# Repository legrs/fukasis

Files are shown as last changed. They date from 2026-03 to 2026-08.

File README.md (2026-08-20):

<h3 align="center" style="margin:0;"> FUKASIS</h3>
<p align="center"> <strong>F</strong>ree <strong>U</strong>niversal <strong>K</strong>it for <strong>A</strong>stro-<strong>S</strong>pectroscopic <strong>I</strong>maging <strong>S</strong>ystem </p>

<p align="right">最終更新日：2026 08/20</p>

<!--### このrepositoryは現在整備途中です。完了するまでしばらくお待ちください。 2026/3/31-->

このREADME.mdはかなり長くなってしまいました。右上にあるGithubの目次機能などを使うと読みやすくなると思います

## はじめに Introduction

**天体用低分散分光システム FUKASIS** は、安価かつ手軽に運用可能な、オープンソースの天体観測用の簡易分光システムです。

<table style="border:1px solid #00000000; font-weight:900; font-size:0.8rem;">
  <tr style="border:1px solid #00000000;">
    <td align="center" style="border:1px solid #00000000;">
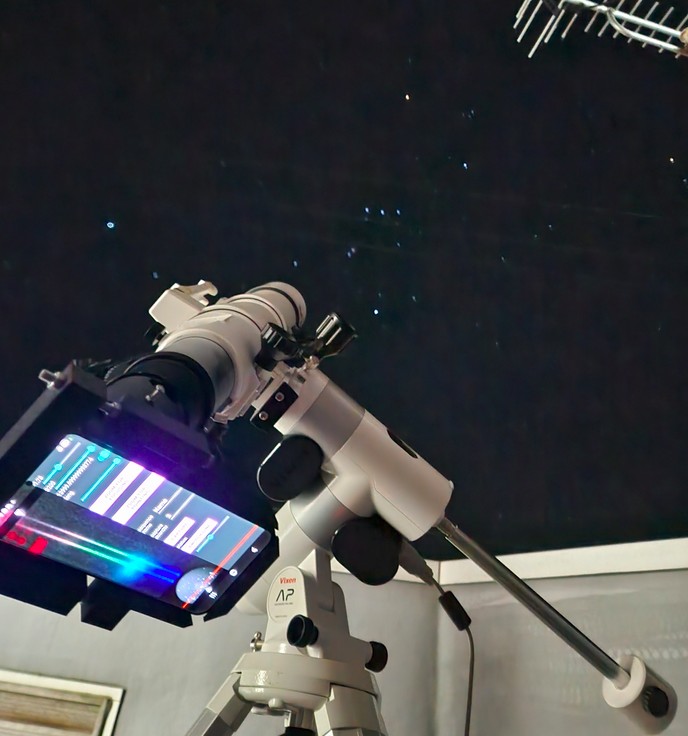
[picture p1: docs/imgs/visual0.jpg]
画像1
      
      <br>
        <p>FUKASISでM42をスリットレス分光している様子。2026-02-17</p>
    </td>
    <td align="center" style="border:1px solid #00000000;">
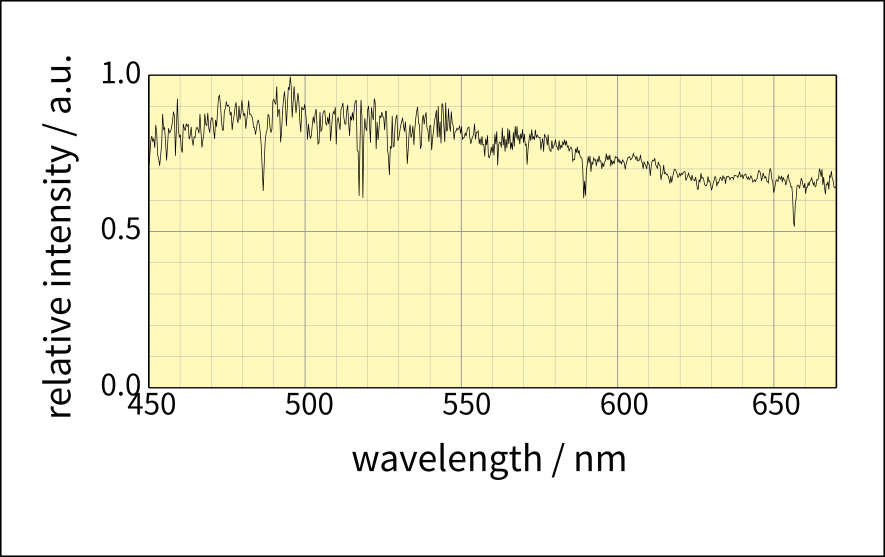
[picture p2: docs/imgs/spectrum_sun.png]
画像2
      
      <br>
        <p>FUKASISによって得られた太陽のスペクトル。多数のFraunhofer線が確認できる。D線も分解している。2026-02-16</p>
    </td>
  </tr>
</table>

### 特徴 Features

撮像にスマートフォンを使用し、専用アプリによって撮影・一次処理・波長感度校正・スペクトル出力まで完結することを最大の特徴とします。

- オープンソース (MITライセンス)
- 安価 (約3万円で制作可能)
- 手軽な運用 (分光器内で撮影と処理が完結)
- 低分散 (可視光全域)

### 主要諸元 Specs

| 名称 | 値 | 備考 |
| ---- | ---- | ---- |
| 名称 | FUKASIS | Free Universal Kit for Astro-Spectroscopic Imaging System
| 波長分解能 $R$ | &ndash; $600$ | 部分的には1000を超える
| 観測波長域 | $450\ \mathrm{nm}$ &ndash; $670\ \mathrm{nm}$ |
| 重量 | $400\ \mathrm{g}$ 程度 | 3D印刷時の充填密度やネジに依存 |
| スリット幅 | 可変 |
| 視準器 | Scopetech Ke25mm |
| 結像鏡 | Galaxy S22 広角カメラ | 広角カメラは中央のカメラを指す |
| 検出器 | Galaxy S22 広角カメラ | 広角カメラは中央のカメラを指す | 
| 分散素子 | 回折格子 $1800\ \mathrm{lines/mm}$ | Aliespressで購入<br>  (Professional fresnel len factory Store) | 
| 取り付け径 | $2\ \mathrm{inch}$ | 
| 制作にかかる費用 | $3,300$ 円 | 実際に制作した時の概算(ネジ類・フィラメント代を除く) |

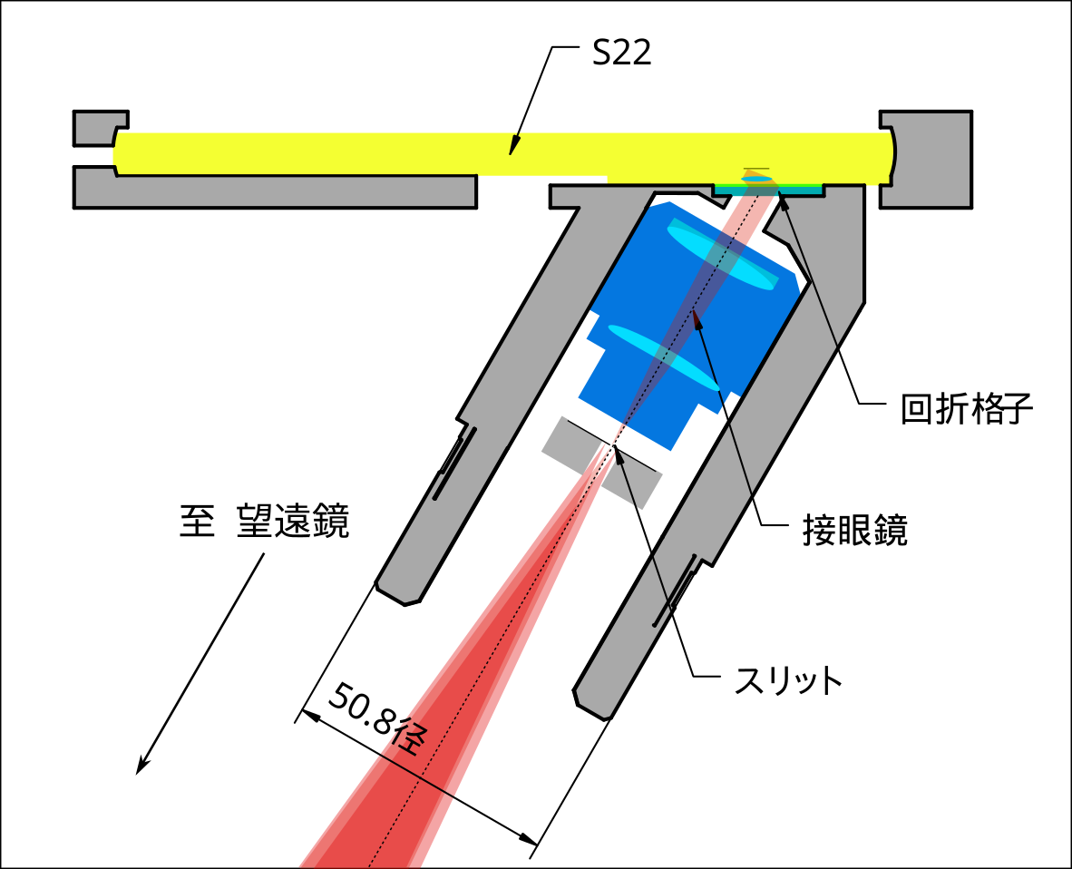
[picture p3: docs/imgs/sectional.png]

<br>

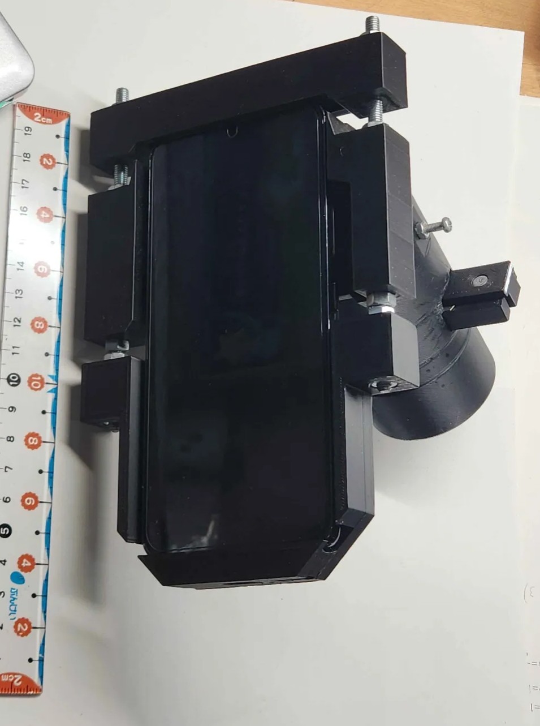
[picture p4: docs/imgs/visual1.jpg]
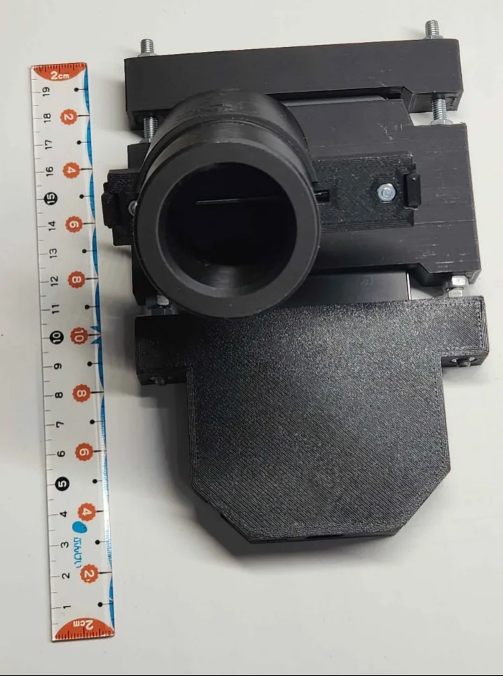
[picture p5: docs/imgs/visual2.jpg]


<br><br><br><br>

## 必要なもの Requirements

### 望遠鏡系
天体など、淡い物体のの分光をする場合は必須となります。とくに指定はありませんが、以下の条件を満たす必要があります。

- $2\ \mathrm{inch}$径で取り付けられる

当たり前ですが、長時間露光するときは自動追尾システム(赤道儀など)があったほうがいいです

### スマートフォン [ Galaxy S22 ]
**Galaxy S22**を前提に設計されています。中古品なら3万円程度で手に入ります。

その他のスマートフォンを使用する場合、筐体の設計・検出器の感度測定はもちろん、専用アプリケーション(以降、FUKASIS-app)もビルドし直す必要がある可能性があります。性能も変わると思われます。\
(もしいい感じのスマホを見つけたらぜひ教えてください。実はS22が最適とは思っていません。)

設計をいじりたい場合は[ドキュメント](#ドキュメント-documents)をご参照ください

### 透過型回折格子 厚さ2mm以下 

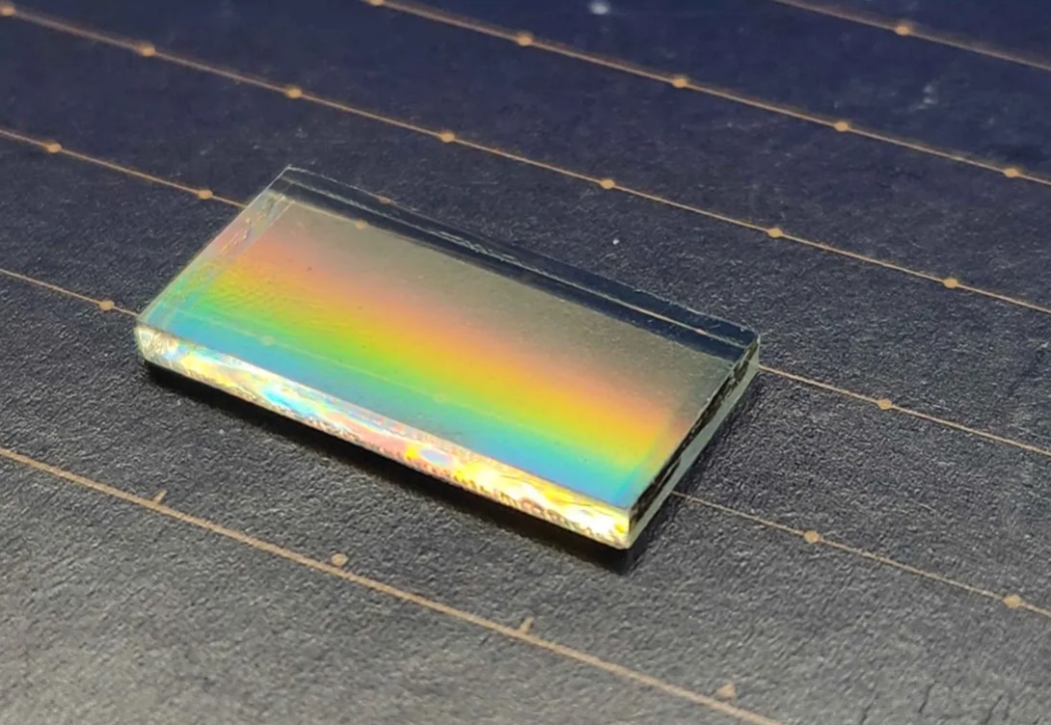
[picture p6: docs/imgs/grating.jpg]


Aliexpressで購入できる、**20 * 15 * 2 mm 格子数1800 lines/mmのガラス回折格子**用に設計されています。3000円ぐらいで買えました

これ以外のサイズの回折格子を使用したい場合、`hardware/cad/main.FCStd`の`[print]main`オブジェクトの
かなり下の階層にある`grating-mold`を調整してください。
ただし、**厚さが2mm以上の回折格子を使う場合、スマートフォンがS22のときに観測波長域が狭くなったり、
0次光がズレる可能性があります**。

また、FUKASIS-appの撮影時のプレビューは格子数 $1800 \ \mathrm{lines/mm}$ に合わせてあります。それ以外の格子数の回折格子を使う場合は以下の点に注意してください。

- 快適なプレビューのためには、FUKASIS-appをビルドし直す必要があるかもしれません
- 分解能 $R=600$ は達成できない可能性があります
- 観測波長域(とくに長波長側)が狭まる可能性があります

### 接眼鏡 [ Ke25mm ]
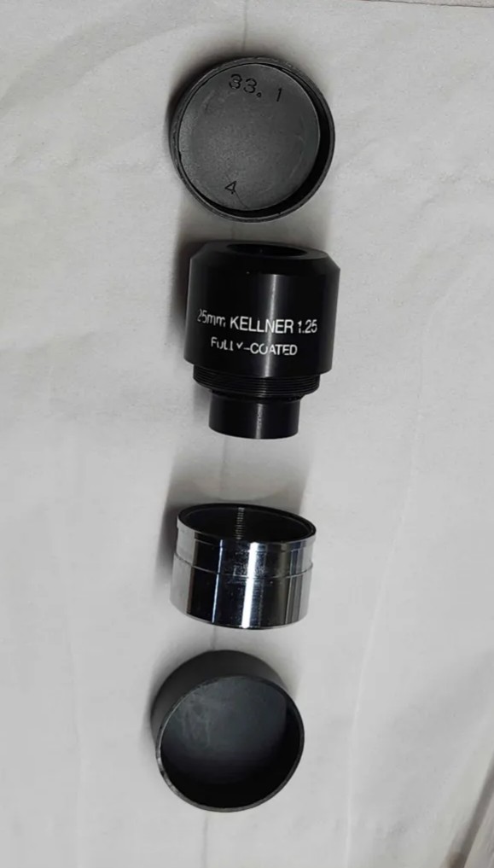
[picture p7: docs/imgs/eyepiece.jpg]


**Scopetech Ke25mm** 接眼鏡を前提にしています。スターベースオリジナルのKe-25mm接眼鏡も、おそらくほぼ同一のため使えると思います(試していません)

Ke20mmやKe-20mmについては、分解能 $R=600$ を達成できない可能性はありますが、代用は可能と思います。

### スリット [ 9mmカッター刃 * 2 ]
スリットは、3Dプリンタ製の構造体に9mm(最も標準的な刃です)のカッター刃を2枚対向させて作成します。

`slit-body.stl` `slit-fixer1.stl` `slit-fixer2.stl`

を印刷してください。これらファイルの場所は[準備](#準備-setup)を参照してください。\
`slit-fixer`は、ネジの頭がくる側を下にして印刷してください。なるべく壁を厚くしてスライスすると良いです．

サイズの不都合などで後から加工する場合は，彫刻刀をおすすめします

### 筐体 
//img

筐体は3Dプリンタ製(FDM)を想定していますが、形さえ作れてかつ強度・剛性が十分ならばどんな方法でも良いと思います

`main.stl` `ue.stl` `shita.stl` 

をそれぞれ1つづつ印刷してください。これらファイルの場所は[準備](#準備-setup)を参照してください。

印刷の際は以下の要件を満たしてください。

- 出力品質 $0.2 \ \mathrm{mm}$ 以下
- wall4ライン以上
- 充填密度 $50 \ \%$ 以上

`main.stl`は印刷の向きに迷うかもしれません。下の画像のような向きを推奨します。
この向きでは、筒にはサポートをつけたほうがいいです。\
mainはかなり印刷が難しいかもしれません…(私はかなり苦労しました)

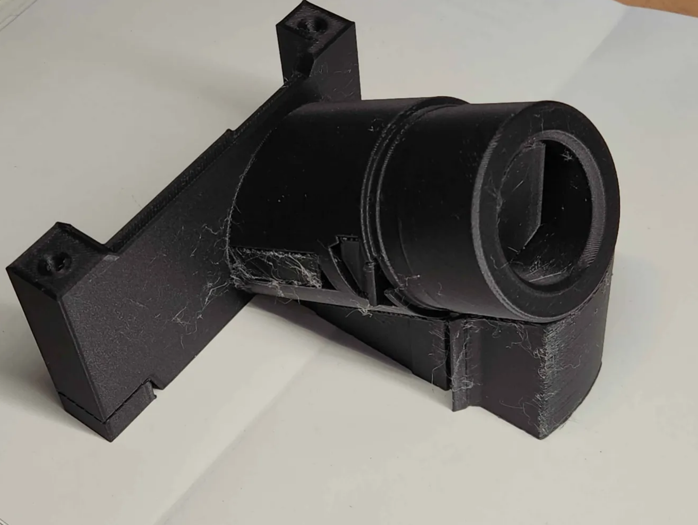
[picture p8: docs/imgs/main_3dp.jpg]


推奨フィラメントは黒色のPLAです。
黒色以外のフィラメントを使う場合、光路を黒く塗装することをお勧めします。

3Dプリンタを持っていないという方のために、**JLC3DP**というオンラインの3Dプリントサービス
が存在することを、紹介だけしておきます。(私は使ったことがないので詳しい説明はできません。すみません…)

### ネジ類

構造用 : 
- M5全ネジ 長さ $120 \ \mathrm{mm}$ 以上, $2$本 (あんまり長いと邪魔になるし重くなります。
    $200 \ \mathrm{mm}$ 以内を推奨します。いちばんいいのは $130\ \mathrm{mm}$ ぐらいです)\
    頭が六角形でナットと同サイズのネジがあればそちらのほうが良いです。その場合M5ナットは8つで済みます
- M5ナット $10$ 個

接眼鏡固定用 : 
- M3ネジ 長さ $12\ \mathrm{mm}$ 以上 $1$, 本
- M3ナット $1$ つ

スリット固定用 : 
- M3ネジ 長さ $8\ \mathrm{mm}$ -- $11\ \mathrm{mm}$, $2$本, 頭が1mm以下の超低頭ネジが好ましいです。
- M3ナット $2$ つ

### 蛍光灯など、輝線の出る光源

感度校正と、ピント調整で使います。前者は観測波長域全体に合計4本以上の輝線が欲しいですが、後者は輝線が1本あれば大丈夫です。
**3波長型の蛍光灯や水銀灯ならまず間違い無いです。** 殺菌灯は輝線の数が少ないので使えるか分かりませんが、試す価値はあると思います。

建物がLED化されているとこれはちょっと困るかもしれません…
その場合は、まずFraunhofer線が候補になります(昼間もしくは月夜である必要がありますが、どんな場所でも使えるのがメリットです。太陽が光源ならなんでもいいので青空でも曇り空でも問題ないのがいいですね)

身近にあるものでは、電源タップについていたりするオレンジ色のランプ(ネオンランプ)ホタルスイッチやパイロットランプが使えないこともないです。(少し長波長側に偏りすぎですが…)
なお分光してみて連続光っぽかったら、それはLED式の新しいタイプなので諦めてください

資金に余裕があったり既に所持しているなら、Hg/ArランプとかHe/Xeランプみたいな、実際の波長校正によく使われる光源を導入するのもいいのかもしれません。
ただ私は実物を見たことないので何とも言えません！

<!--(買ったことはないですが、けっこうなお値段しますよね…？正直この程度の分光器にそこまでにガチの光源使うのは個人的には心地良くありませんが…)-->

<br><br><br><br>

# 準備 Setup

Releasesから、最新の`release.zip`ファイルをダウンロードしてください。\
展開すると、中身は以下のようになっています。

```release.zip
release/
├── app-release.apk
├── sensit_distr.csv
└── stl/
    ├── main.stl
    ├── shita.stl
    ├── slit-body.stl
    ├── slit-fixer1.stl
    ├── slit-fixer2.stl
    └── ue.stl

```

### ハードウェア Hardware

[必要なもの Requirements](#必要なもの-requirements)で示したとおりに、`.stl`を印刷します。

* **組立て**

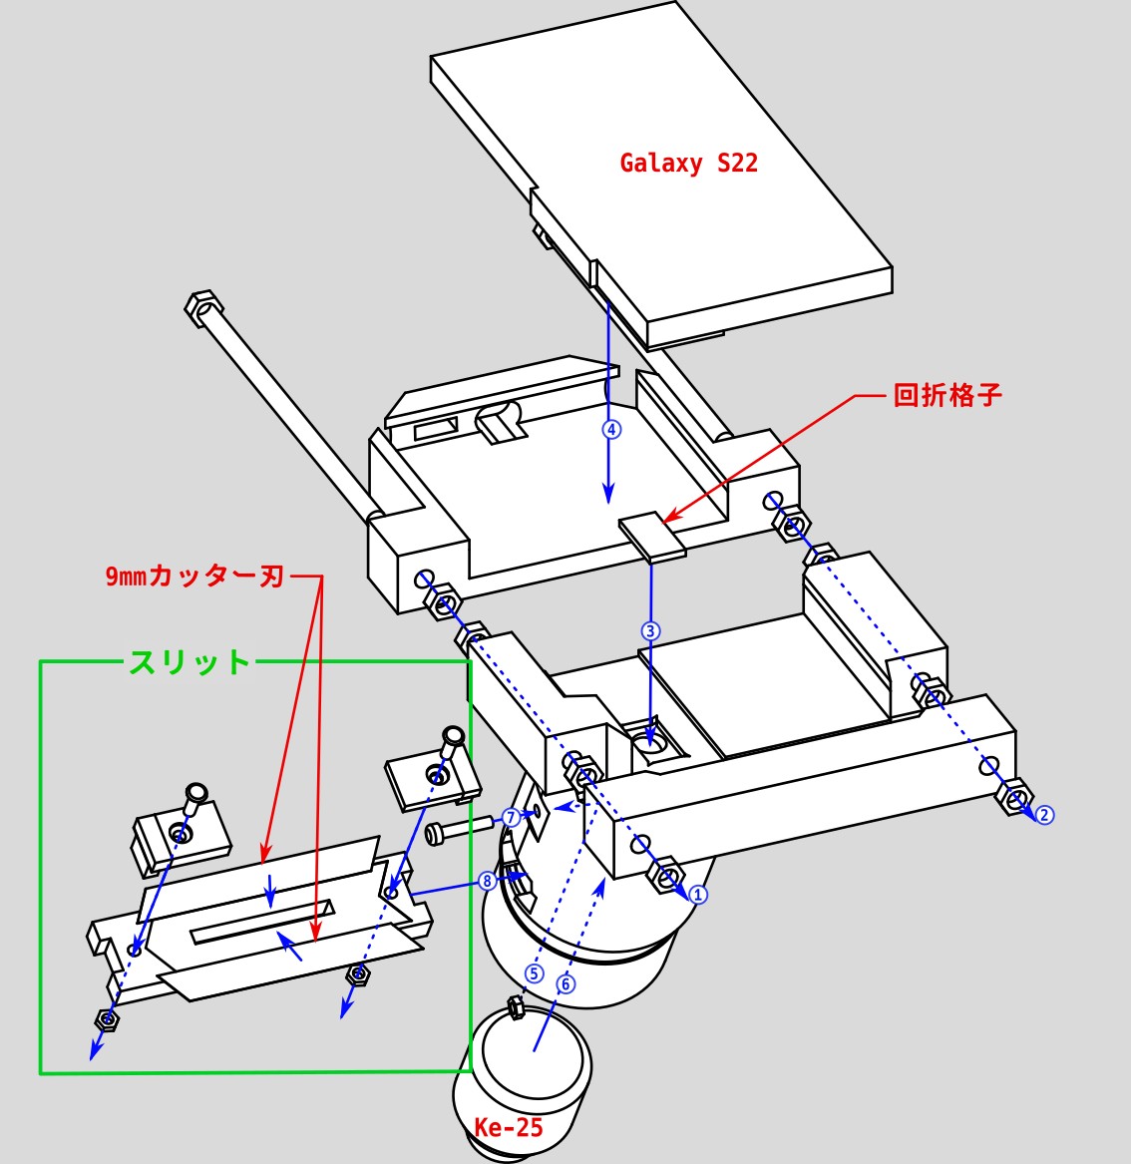
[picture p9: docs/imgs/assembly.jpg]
組立。
    

    本体とスリットを画像のように組み立ててください。

    `slit-fixer1`にM3低頭ネジを入れてみて、頭が出張ってしまうようであれば、彫刻刀やカッターなどで
    、`slit-fixer1`の頭用の溝を削ってください。(プリントの時点でここを薄く作ってしまうと強度的な問題が発生します。)

    回折格子はgrating面(溝が刻まれている方の面)をスマホカメラ側にしてください。

    s22の真ん中のカメラがだいたい回折格子のところの穴に合うような位置で`main.stl`は固定してください。(細かい調整は次でやります)

    Ke-25接眼鏡は、スリーブ(塗装されていない金属の筒)を取りはずし、スリーブがついていた側がスリット側になるように入れます

    * grating面の判別

        レーザー光を斜めに入射させて1次回折の反射光を見るとすぐに分かります。
        画像のように、grating面が上なら1次回折光は2重になります。

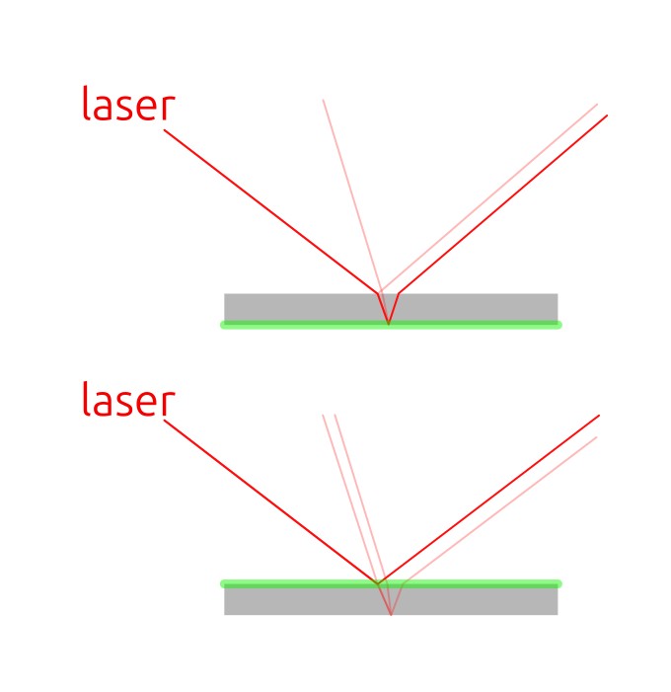
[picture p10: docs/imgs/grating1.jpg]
grating面が上なら1次回折光は2重になります
        

        レーザーポインタが無い場合は点光源に近いものを用意してください。
        左の画像をダウンロードしてS22の画面に表示し(最大輝度にするとよい)、暗いところで反射光を確認します。
        
        白い丸をおいただけ
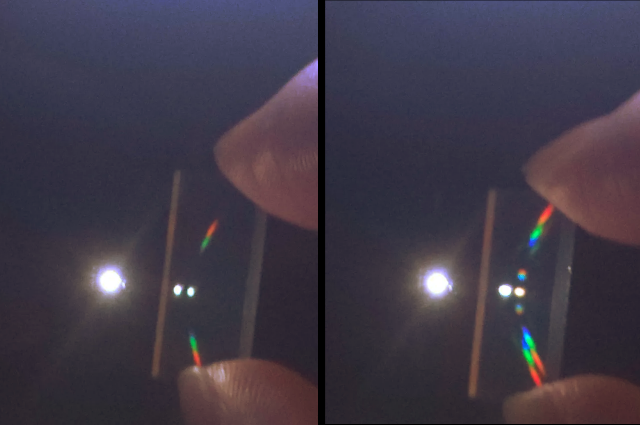
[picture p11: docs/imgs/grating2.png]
こうなります。右はgrating面が手前。撮影大変だった
        

        (この方法もっと簡単なの知ってる方いたら教えてください)

        grating面が分かったらその面の端にマーカーなどで小さく印をつけておくと、次回以降楽になって良いです。

* **調整**
    
    とりあえずスマホまで組み立たったら、スマホの左右(長辺側)の余り幅が均等になるようにして(中央に配置するという意味)、`ue.stl`側のナットで締めます。

    次に`main.stl`の位置調整をします。`main.stl`を締めつけているナットをすべて緩めて、スライドできる状態にしてください。
    望遠鏡の取り付け部側から除いて、だいたい真ん中あたりにカメラのレンズが来るように、`main.stl`を動かします。あとは固定して完了です\
    (これは、多少ズレても問題ないのでそんなに追い込む必要はないです。)

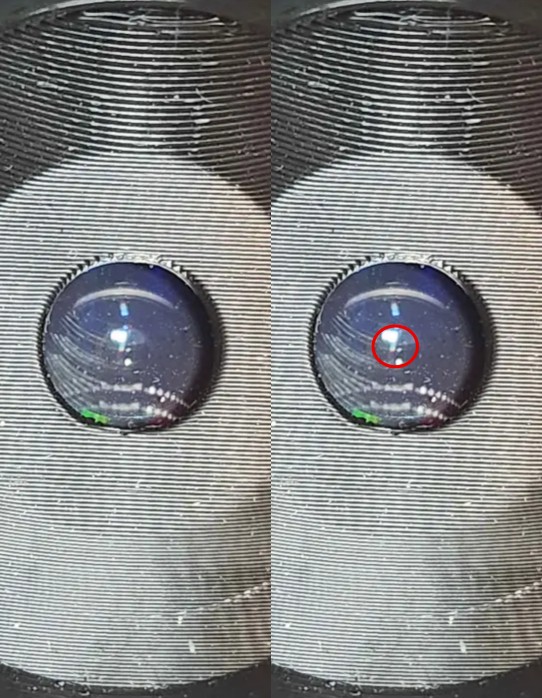
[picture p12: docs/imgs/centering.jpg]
反射で見づらいですが…
    

### ソフトウェア Software

まず、Files by Googleをインストールしてください。FUKASIS-appのインストールに使います。\
内部ストレージが直接覗けるため、FUKASIS-appの運用にも便利です。
(撮影データなどの状態を確認する手段がFUKASIS-app内には無く、ストレージの状態が
分からないと困ることあるためです。)

* **FUKASIS-appのインストール**

    `app-release.apk`をfiles by googleで開こうとすると、権限の許可を求められると思うので、「設定」をタップし、権限を許可します。
    もういちどfiles by googleでapkファイルをタップすれば、自動的にインストールが開始されます。
    
    アプリを開くと、初回は自動的に設定画面に飛ばされます。これはアプリを再インストールしたときに、
    以前の観測データが開けなくなってしまうのを防ぐためのファイルの操作権限です。\
    許可をしてアプリに戻ってください。以降は表示されません。

* **ストレージの状態を見る**
    
    Files By Googleのトップの画面で一番下にスクロールすると、Internal Storage(内部ストレージ)があります。
    そこからこの`README.md`で示すpathにたどりつけます。
    例えば，`Internal_Storage/Documents/FUKASIS-app/imgs`，これは撮像した写真たちがあるディレクトリになります．

* **その他の設定**
    
    設定アプリの、「ディスプレイ」の「明るさ自動調整」をオフにすることをお勧めします。
    (観測時は画面輝度を自由に変えられたほうが便利なため)

    「バッテリー」の「省電力モード」をオンにすると、若干電池持ちが良くなるのでこれもやってもいいと思います。

<br><br><br><br>

# 使い方 Usage

**[注意](#注意-Attention)を必ず読んでから使用してください**

### FUKASIS-appの説明

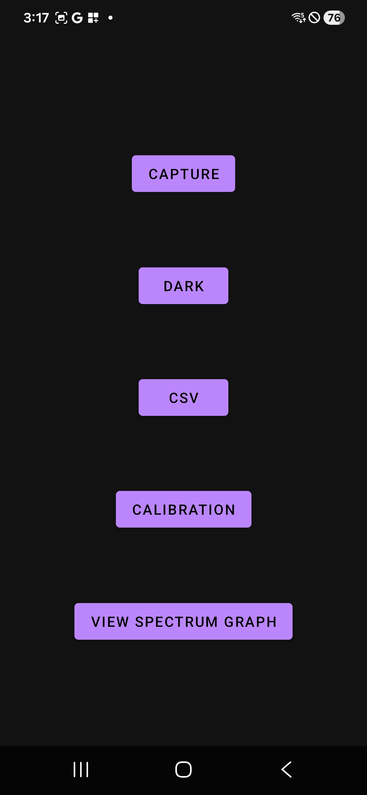
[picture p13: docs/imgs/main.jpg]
main画面


これがmain画面です。ボタンと遷移先の画面の関係は

**CAPTURE** → **capture画面**(撮像用)

**DARK** → **dark画面**(ダーク減算用)

**CSV** → **csv画面**(スペクトル出力用)

**CALIBRATION** → **calibration画面**(波長校正データ作成用)

**VIEW SPECTRUM GRAPH** → **view画面**(スペクトル表示用)

このようになっています。

#### capture画面 :
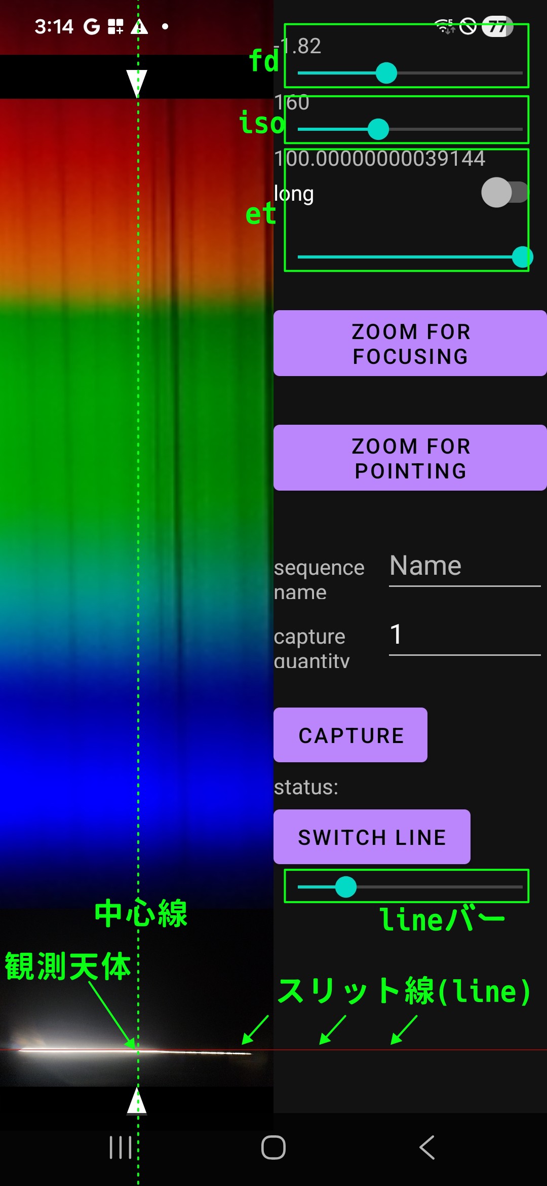
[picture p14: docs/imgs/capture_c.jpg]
capture画面


撮像(観測)のための画面です。

* **fdバー**

    fd(Focal Distance)の調整バーです。0が無限遠で、負の値は無限遠のときより焦点距離が長くなる設定です(おそらく)。

    -1.7ぐらいで合えば正常です。

* **isoバー**

    ISO感度のバーですl。
    
* **etバー**

    露光時間(Exposure Time)を調整するバーです。10を底とする指数関数になっています。

    デフォルトで $1\ \mathrm{ms}$ -- $100\ \mathrm{ms}$ の範囲です。
    **long**にチェックを入れると、 $100\ \mathrm{ms}$ -- $1400\ \mathrm{ms}$ の範囲になります。
    (このせまいバーで全範囲をいちどに指定しようとするとあまりに不便だったので…)

    露光時間についてですが、だいたい次の撮像に**露光時間の1.5倍**ぐらいの時間がかかってしまっています。(おそらく自動的にダーク減算が行われているからだと見ています)
    これについてはいろいろ試みましたが、解決できませんでした。後からダーク減算することを考えるとかなりの無駄なので、なんとかしたいのですが…

* **ZOOM FOR FOCUSING**
    
    輝線を拡大してfdを調整時しやすくするものです。撮影時は解除してください>(toggle buttonになっています)

* **ZOOM FOR POINTING**
    
    天体をスリット線に正確に導入するために、0次光を拡大します。撮影時は解除してください>(toggle buttonになっています)

* **SWITCH LINE**
    
    スリット線の可視ををtoggleします

* **lineバー**
    
    スリット線の位置を調整します。

#### dark画面 :
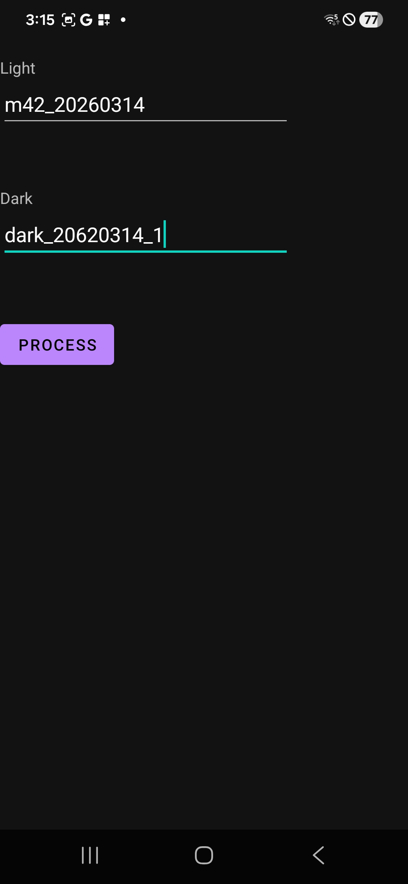
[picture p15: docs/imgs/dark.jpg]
dark画面


ダーク減算をする画面です。

上にライトフレームの名前、下にダークフレームの名前を入れて**PROCESS**を押すだけです。(とくに何も表示されずに処理が完了します)

#### csv画面 :
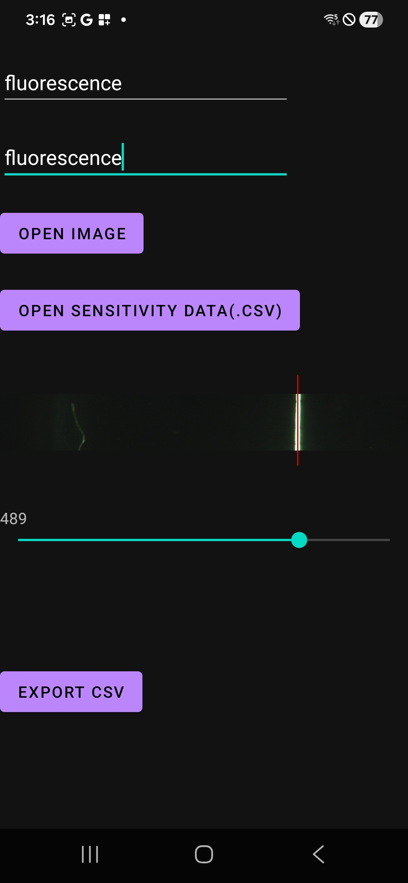
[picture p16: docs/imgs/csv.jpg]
csv画面


スペクトル出力に使う画面です。

上に観測の名前、下には、calibration画面で入れた「校正データの名前」を入れます。

#### calibration画面 :
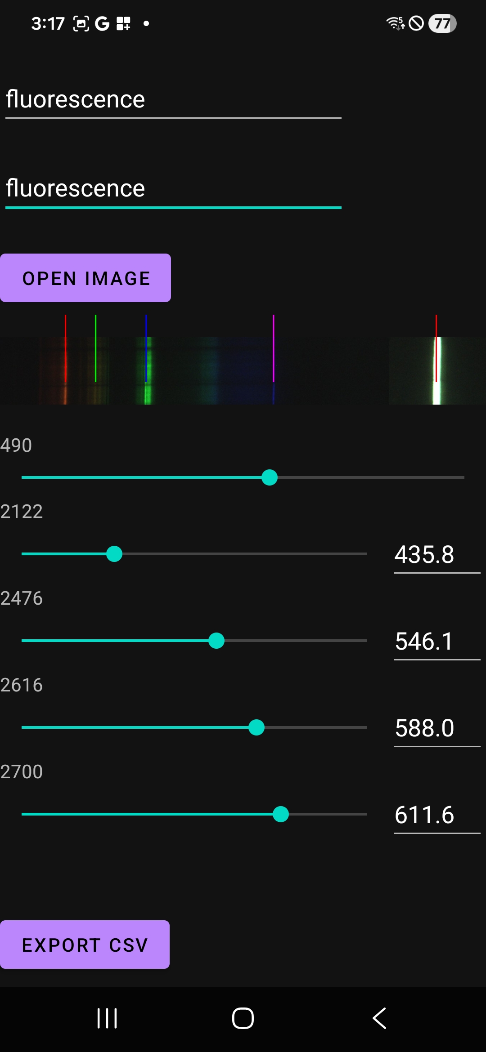
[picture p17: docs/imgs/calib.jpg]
calibration画面


上に校正用観測の名前、下には「校正データの名前」を入れます。

一番上のバーが0次光の位置(赤)を示すバーです。\
それ以外はバーの右側の波長と合うような位置に動かします。

3次近似なので4つありますが、「2次でもいい」「4本もない…」という場合は、同じ波長を2つのバーに入力して全く同じ位置に持っていきましょう

#### view画面 :
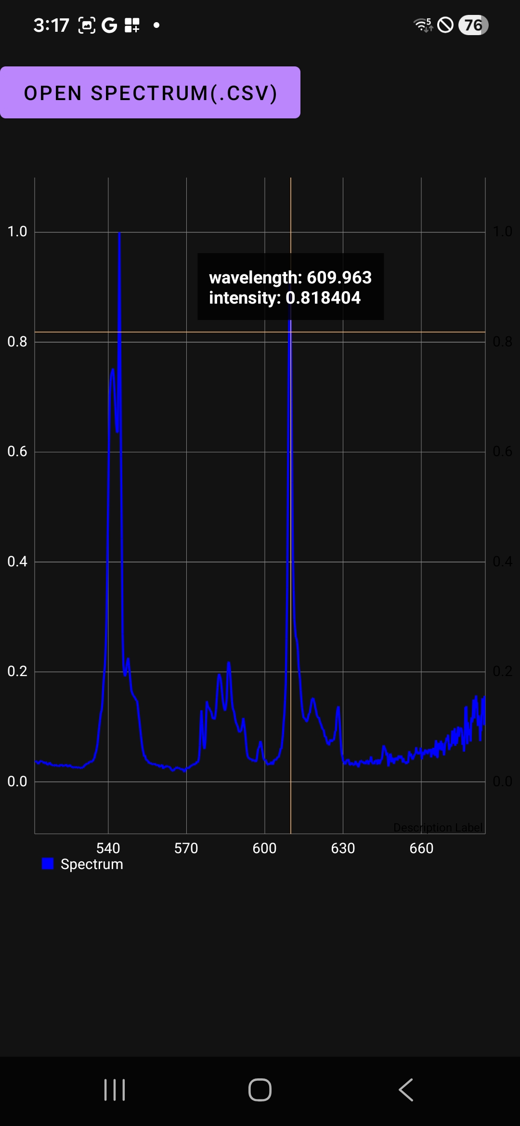
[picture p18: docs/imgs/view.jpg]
view画面


スペクトルの表示用の画面です。機能は拡大・縮小・値表示のみです。

<br><br>

### 扱い方
- スリットは`slit-fixer2`(厚い方)の側から引き抜いてください。(`slit-fixer1`が接眼鏡の下を通るように)\
    逆に`slit-fixer2`は接眼鏡の下を通過できないので、スリットの脱落防止ストッパーとして機能します．

- 淡い天体の撮影時に周りが明るい場合は、分光器全体(とくにslit周辺)をアルミホイルなどで覆って、十分に遮光してください

- アプリの電池消費が激しい上に、Galaxy S22は電池持ちが悪いモデルなので、充電しながらの観測を推奨します

### 調整
主にコリメータ関係のピント調整です。
1. スリットを付けます。
1. 接眼鏡の固定ネジをいちど緩め、画像のように重力で`slit-fixer1`と接触するようにしてください。
1. 接眼鏡を固定します(ズレないよう強めに。Ke-25mmは割と丈夫です)
1. スリットを限界まで細くします。
1. 輝線を持つ光源に向けます
1. FUKASIS-appの**capture画面**を開きます。
1. 白飛びがないよう、適正な明るさにします。
1. **ZOOM**ボタンを押して、輝線の幅を見やすくします
1. 上のfdバーを動かして、輝線が最も細くなる値を見つけます。(-1.7ぐらいになると思います)(接眼鏡など取り付け直さない限りほぼ変化しません。毎回やると面倒なのでメモしたほうがいいです)

### 本観測・処理
実際の分光観測の手順です。

おおまかに\
(1)ライトフレーム撮影(capture画面)\
(2)ダークフレーム撮影(capture画面)\
(3)処理(dark画面,csv画面)\
という流れになります。

1. **capture画面** を開いておきます
1. 望遠鏡に接続します(2 inch径です)
1. スリットを指し込んておきます。
1. スリットの位置が分かるように適当に照らすなどしてます\
    下のslitバーを動かしてスリットの位置に赤線が来るようにします
1. スリットを外します
1. 赤線と、上下の白い三角形で示す中心線の交点となる位置に目標天体が来るように導入します。(この中心線上、幅80pxのスペクトルを読むことになります。)
1. スリットを差し込みます ( ここで、「暗すぎる」などの理由からスリット幅を広げることもあるかと思いますが、それを行った場合は1からやり直してください )
1. isoバー(感度)とetバー(露光時間)で明るさを調整します。**どのチャンネルもサチらないように気をつけてください**
1. 観測の名前を**sequence name**欄に入力します(`alphaOri_260314_1` みたいに)。\
    撮影枚数を**capture quantity**欄に入力します
1. **CAPTURE**ボタンを押します！撮影が開始されます。\
    1枚撮影が終わるたびに長音3回のBeep音が鳴ります(Beep-Beep-Beep)。\
    capture sequenceが終わると長音6回のBeep音が鳴ります(Beep-Beep-Beep-Beep-Beep-Beep)\
    画像は `Internal_Storage/Documents/FUKASIS-app/imgs`下にsequence nameのディレクトリが作成され、保存されます。それぞれのraw画像(.dng)と`stacked.tif`と`stacked.jpg`が保存されます。
<br><br>
1. 分光器を遮光して暗くした状態で、観測と同じ方法でダークフレームをとります。同じ露光時間・ISO感度にしてください。名前は`dark_20260314`にようにすると良いです。 なおダークフレームを撮らなくてもスペクトル出力はできます。
    スリットの差し込み口から光が入らないよう気をつけてください。
1. **dark画面**に移ります\
    観測の名前とダークフレームの名前を入れて、**PROCESS**を押します。減算されて`Internal_Storage/Documents/FUKASIS-app/imgs/観測の名前/darked.tif`が保存されます。
1. **csv画面**に移ります
1. 観測の名前を**Sequence Name**に入力し、**OPEN IMAGE**と押します。
1. スライダーを使って0次光の部分に赤色のラインを載せます。
1. **Calibration Dana Name** に**波長校正データ**(これは下のセクションで作成するものです)の名前を入力。**OPEN SENSITIVITY DATA(.csv)** から、感度データを選択します。Relaaseの中の`sensit_distr.csv`がそれです。([準備](#準備-setup))
1. **EXPORT CSV** ボタンを押します。`Internal_Storage/Documents/FUKASIS-app/csv/spectrum/`下にスペクトルが保存されます。

### 校正観測・処理
波長校正の観測です。組み直したときにのみやる想定ですが、もしかしたら観測毎にやるのがベストかもしれません。このあたりまだ検証が済み切っていなくてすみません…
1. 本観測と同様の手順で(3 &ndash; 8 は省略)、蛍光灯や太陽の反射/散乱光など波長校正用の光源を観測します。**capture quantity**は1枚で良いです。**sequence name**は蛍光灯なら`fluorescent_260314_1`のようにすると分かりやすいかと思います
1. 観測のデータを**calibration画面**で開き、一番上のスライダーを使って0次光の部分に赤色のラインを載せます。
1. 他のスライダーで波長(右側のtextbodと画像上の位置(スライダーで動かす)を対応させていきます。3次のlagrange補間をするので、4本必要です。波長の初期値は蛍光灯のものです。(588.0 nmの輝線は分かりづらいですが、オレンジの輝線が2本並んでいるうちの長波長側のものです)\
    波長の数値は変更できるので，三波長型蛍光灯以外を使う場合は事前に調べて打ち込みましょう．同定がけっこう難しいくて……ここはどうしても苦戦するところです
1. **EXPORT CSV** を押すことで、波長校正データが``に出力されます

### 解析
主にPCや別アプリで行うことを想定していますが、グラフ表示など最低限の機能はFUKASIS-appに搭載してありあす。\

1. **view画面** に移ります。
1. **OPEN SPECTRUM(.csv)** から、スペクトルファイルを開きます
1. スペクトルが表示されます。拡大したり値を呼んだりできます。

csvは最初の2行にヘッダーがあります。

1行目がsequence name, 時刻, 撮影の設定などです。\
2行目はラベルを示します。`wavelength/nm,relative intensity(0.0 -- 1.0)`となっています。波長と相対強度で、相対強度はデータの中でもっとも大きな値が$1.0$となるような単位になっています。\
以降はカンマで区切られた2組のデータが並びます。

<br><br><br><br>

# 注意 Attention
分光器を壊さないための注意点が含まれています。**必ず読んでください。**

- **太陽の観測では望遠鏡を使わないでください！** **センサの焼損**や**スリットの融解**などの重大な事故に繋がるおそれがあります。\
    太陽など、明るいものは単体で十分観測できます。

- **長時間の撮影時は画面を暗くしてください！** Galaxy S22はOLED(有機ELのディスプレイ)なので、高い輝度で同じ画面を表示し続けると**burn-in(焼き付き**)が発生する恐れがあります。

- 紹介したAliexpressの回折格子は、replica diffraction gratingというものに分類され、本体はガラスですが、gratingの部分は製造が安価な樹脂製となっています。\
    大変傷付きやすいので、grating面を直接触らないようにしてください。(多少の傷で観測に支障は出ないと思いますが…たまに剥れることもあるので…)

- 本分光器による観測結果は**正確な**スペクトルを**保証しません**。観測データを使用する際は自己責任でお願いします。

<br><br><br><br>

# トラブルシューティング Trouble-Shooting

### 望遠鏡に取り付けるとピントが合わない
ドローチューブを限界まで引き出しても、望遠鏡の焦点面がスリットよりもスマホ側に来てしまうことがあります。これは残念ですが、2 inch(31.7mm)の望遠鏡用の延長筒を買ってください(延長筒を3Dプリンタで制作するのは剛性の観点からお勧めしません)

### capture画面でプレビューが固まった
実装がしっかりしていないからか、よく固まります。そのときはmain画面に戻ってからもういちどcapture画面に入って設定しなおしてください

### fdバーを端まで動かしてもピントが合わない
接眼鏡のスリット側の筒か、スリットの固定具をやすりで少し削ると良くなるかもしれません。\
一度fdを-1.7ぐらいにして、スリットを完全に入れた状態で、固定ネジを緩めて、ピントが合う位置まで接眼鏡を動かしてみてください。この接眼鏡の位置でスリットが取り外せるぐらい削れば十分です。
(固定ネジと逆側の窓から接眼鏡にアクセスできます)

Ke-25mm接眼鏡のスリーブを取りはずしたときに出てくる黒い筒は視野環で、終端がちょうど焦点面になっています。
それをスリット(カッター刃の位置)から離しているためにfdをゼロ(無限遠)ではなく負の値にしているわけですが、
それにも限界があるのでこのような調整が必須となる場合があります。

<br><br><br><br>

# ドキュメント Documents
設計を変えるためなど、筐体やアプリをいじりたい方は、`./docs/kwsk.md`をご参照ください。不明な点は[お問い合わせください](#お問い合わせ)

<br><br><br><br>

# 名前 Naming
FUKASIS は、開発者の所属する長野県松本深志高等学校地学會の「深志」をベースにしたBackronymです。
最初の**F**reeにちょっと違和感があるかもしれませんが、まあオープンソースの言い変えってことで…

元々部活で使うために開発された分光器だったので、このようなネーミング(高校名)となっています。

<br><br><br><br>

# お問い合わせ
質問・相談・不具合の報告などは、**[Twitter@legrs4073](https://x.com/legrs4073)** 又は **[ktgwyi01@gmail.com](mail:ktgwyi01@gmail.com)** 又は **[本repositoryのIssue](https://github.com/legrs/fukasis/issues)** へお気軽にお寄せください。\
ただし、製作者が大学入試に備えるため2026年度中は更新ができない可能性が高いです(応答はできる限りします)。

(この`README.md`は短期間で作成したもので、自分でもちょっと不親切な出来だと思っています。
何かしら不明な点はあると思うので、気軽に連絡していただければ嬉しいです。)

<br><br><br><br>

# ライセンス License
MITライセンスで公開しています。 Copyright (c) 2026 Tsuyoshi Kobayashi(legrs4073)

好きに中身をいじってもらって構いません。配布は販売は
Copyright表記だけが
義務となります。

これは義務ではないのですが、いじった結果「もっと良いものができた」という場合は**ぜひ公開・配布・販売した上、DMなどで知らせてほしい**です！
些細な変更でも泣いて喜びます

Pull Requestも受けつけています。

---
ここまで読んでくださってありがとうございます。このシステムに興味を示していただけただけで私は嬉しいです。\
この分光器があなたの役に立つことを願っています。

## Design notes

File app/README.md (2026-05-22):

米 時間がないので簡易的な説明になってしまいます．より詳細に知りたい方は twitter@legrs4073まで

全体の構成としては

それぞれのactivityのJavaがあり，
そこに加えて撮影専用の`Cam.java`，
opencvでの処理専用の`native-lib.cpp`．

という形になっています．

- Javaでのファイルの読み書きはMediastoreを使っていて，ユーザーから見える位置に全てのデータを置いています．
- c++側でファイル入出力するときは，file descriptorをJavaから渡しています．
- Cam.javaでは，撮影が終わるたびにImage.Planeの.getBuffer()をc++に渡して，env->GetDirectBufferAddress(buff)してポインタを取得してMatをつくっています．
    それを加算し，capture sequenceが終わると枚数で除算してスタックしています．\
    スタックした画像は`CV_32FC1`のtiffで保存しています．

---

画像処理について

最終的なスペクトル出力(CSV画面での処理)は，
1. スペクトルと直交方向に，一定の幅(makecsv関数のwidth変数)でpixelの値を見て，平均と標準偏差を計算
1. もういちどスペクトルと直交方向に一定の幅でpixelの値を見て，偏差が標準偏差を上回っていなければ加算して平均をとる(sigma-clippingというのでしょうか)
1. 上をスペクトル方向の全pixelで実行(走査)．これで得られる，画像の幅次元のvectorが`pure[channel]`です．channelは0,1,2をとり，そのままb,g,rチャンネルを表します
1. これで得た値は，channel=0,2(bとr)で欠落が発生する(bayer arrayのせい)ので，そこは一次補間します．
1. 各channelの最小値と最大値を出します．各channelで最小値で減算します(最小値が0になります．)
1. 「波長校正ようデータ」の値を使って，Lagrange補間で，位置を波長に変換します．
1. 400 -- 700 nmの範囲で，感度データの値(一次近似)で除算，最大値が1になるよう定数倍して終了

となっています

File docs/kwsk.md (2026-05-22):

repositoryのディレクトリ構成を以下に示します。
```
fukasis/
    ├── app/
    │   ├── app/
    │   ├── README.md
    ├── docs/
    │   ├── imgs/
    │   ├── kwsk.md
    ├── hardware/
    │   ├── cad/
    │   │   └── main.FCStd
    │   └── stl/
    ├── LICENSE
    └── README.md
```

筐体のFreeCADデータ(.FCStd)とFUKASIS-appのソースコードは、それぞれ本repositoryの`app/`と`hardware/cad/`ディレクトリに格納されています。

`fukasis/app/README.md`にはアプリの内部の説明がちょっとだけあります．

## アプリのbuild
Android Studioが必須です．

`クローンしたfukasis/app/local.properties`
この中身を以下のようにしてください．
(pathは環境に依存します．自分の環境でのpathを調べて置き換えてください)
(Windowsの場合はスラッシュもしくはバックスラッシュ2つです．)

```
sdk.dir=Android/Sdkのパス
org.gradle.java.home=jbrのパス
opencv.dir=このrepositoryをcloneしたパス/app/app/src/main/sdk/native/jni
```

これでbuildできるようになるはずです．

## 筐体
このFreeCADのプロジェクトは，残念ながら依存関係もごちゃごちゃしていてあまり良い作りではありません．

ちょっとしたCutぐらいなら問題ないと思いますが，しっかりした編集をするなら，
「これを参考にして作り直す」というのが一番近道になるかもれません．

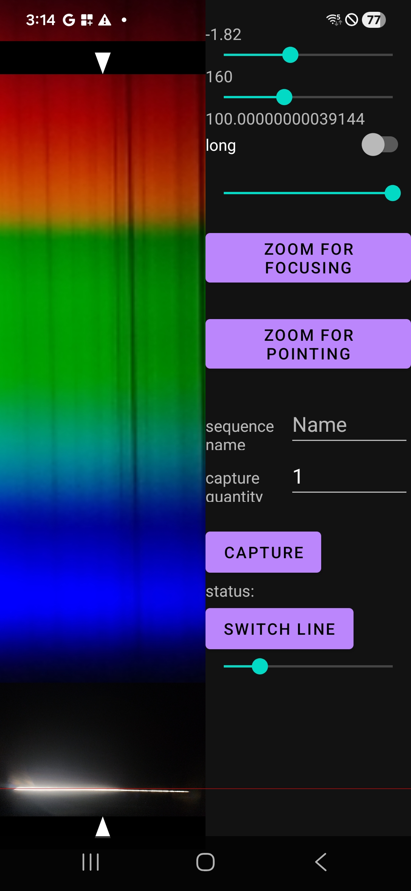
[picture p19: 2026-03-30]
docs/imgs/capture.jpg

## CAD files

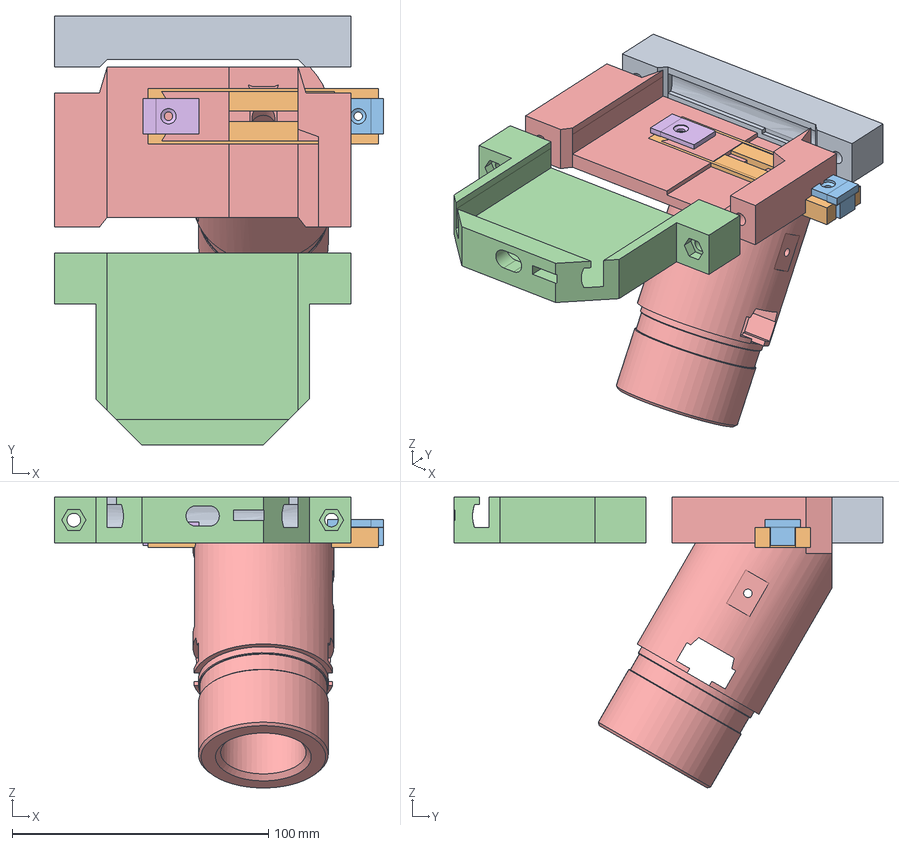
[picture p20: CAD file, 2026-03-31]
hardware/cad/main.FCStd
128.7 x 167.5 x 113.6 mm
[print]ue
[print]slit-body
slit-fixer2
[print]shita
main
slit-fixer1

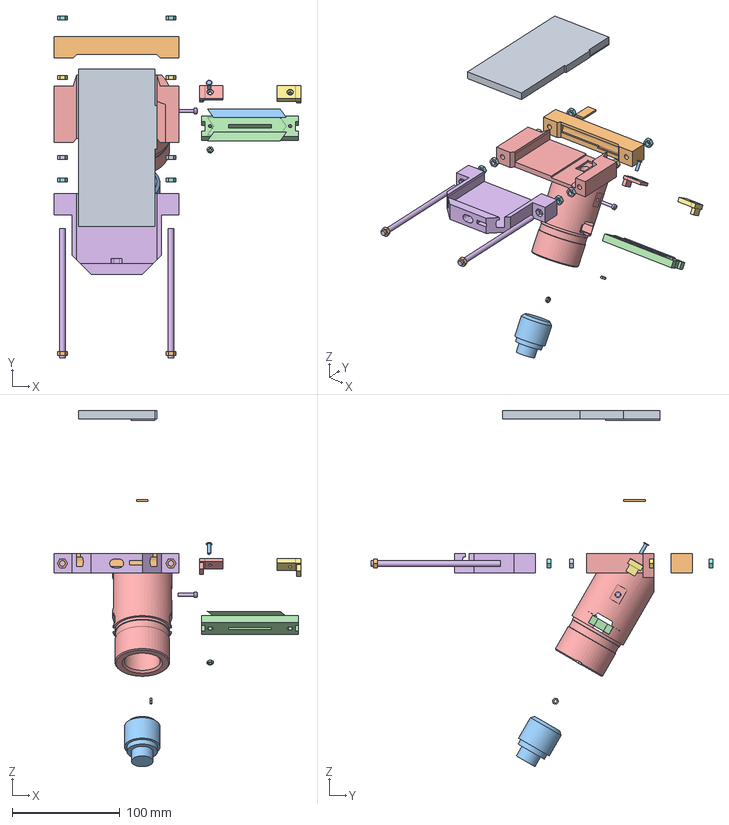
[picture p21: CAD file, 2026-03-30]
hardware/cad/main_tecIllu.FCStd
228.7 x 317.0 x 330.4 mm
smp-model
[print]ue
ke20-model
[print]slit-body
fixer0
[print]shita
fixer1
nut1
camf001
grating
cutter
cutter001
[print]main001
m5
nut2
nut3
nut4
nut5

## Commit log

2026-03-27 complete calibration activity
2026-03-30 add a lot in README
    [main.FCStd, main_tecIllu.FCStd]
2026-03-31 first release!
    [main.FCStd]
